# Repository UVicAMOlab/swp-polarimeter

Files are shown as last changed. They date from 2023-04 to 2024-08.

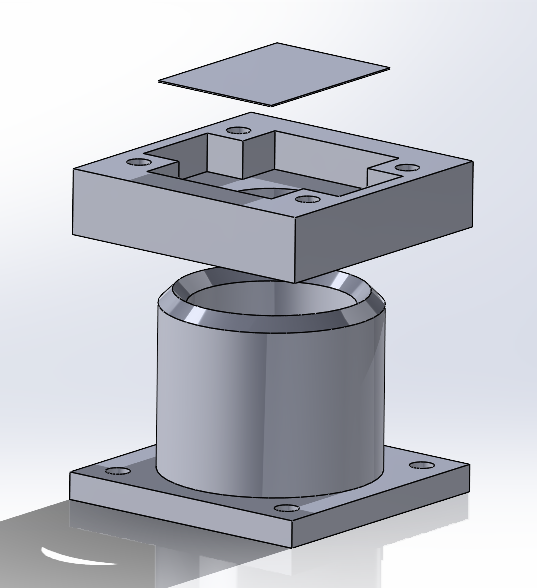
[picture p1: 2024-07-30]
CAD-parts-2024/3D_Printed_Parts/Exploded_View_of_DiodeHousing_with_Polarizer.png

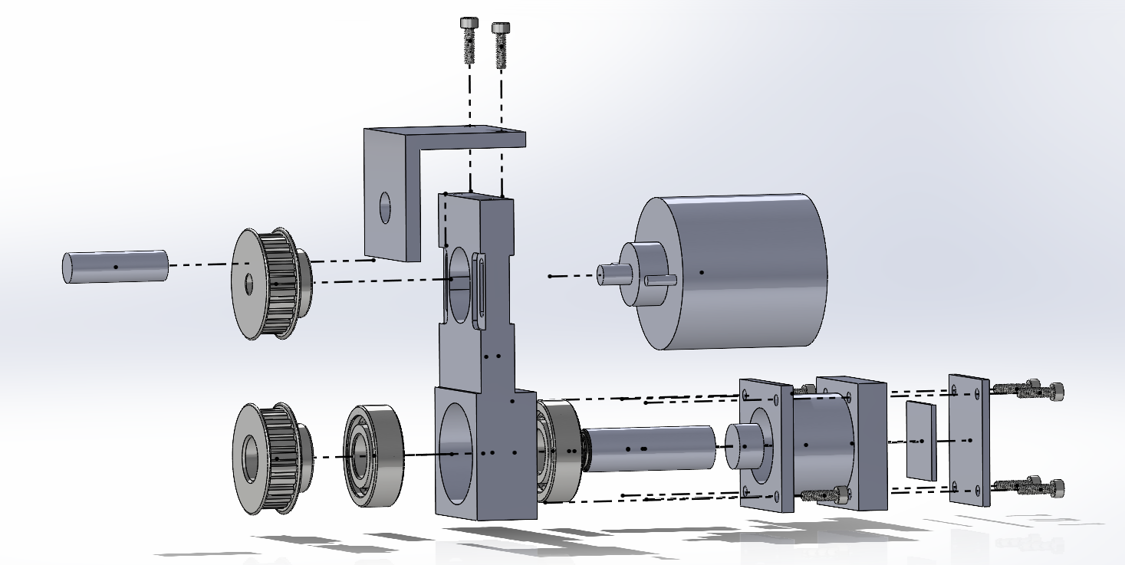
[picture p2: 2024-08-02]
resources-and-documentation/assembly/Mechanical_Assembly_Exploded_View.png

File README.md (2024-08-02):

## Spinning Waveplate Polarimeter

*Using a rotating quarter waveplate, a photodiode, and a few Python scripts, we can produce real-time visualization of the polarization state of incident light. This fully integrated system is easily calibrated and an affordable alternative to other fussy optical technologies making it ideal for research laboratories and educational environments.*

# Real-time Detection of Polarization of Incident Light

Initially, we use the API provided by the DAQ hat to acquire a fixed number of samples for processing; typically, this is 1000 samples at 20 ksps when the waveplate is spinning between 4500 to 5500 RPM. The raw data input is then divided into segments. Each segment is numerically integrated to determine the Fourier coefficients, and furthermore, the Stokes parameters and polarization state. To minimize any statistical errors, the mean result over several segments is considered and the display is refreshed at a rate of 4 Hz.

The reconstruction of the Stokes vector is achieved by calculating the incident intensity upon the rotating waveplate as a function of the rotation angle when aligned horizontally. We assume that the waveplate has some arbitrary retardance instead of considering a precisely calibrated quarter waveplate. Lastly, using the orthogonality of trigonometric functions we can extract the Stokes parameters S<sub>0</sub>, S<sub>1</sub>, S<sub>2</sub> and S<sub>3</sub>. Using the Stokes parameters, the degree of polarization of the incident light is also obtained through a trivial calculation.

Please see our more rigorous [explanation]#(REPLACE WITH PAPER LOCATION) and [analysis](https://github.com/UVicAMOlab/swp-polarimeter/blob/main/resources-and-documentation/analysis/Polarimeter_Analysis.pdf) for more details.

# Information Obtained from Polarimeter

The continuous data input through the Raspberry Pi's MCC DAQ hat along with the included software allows for the real-time determination and visualization of several polarization parameters. These include:

- Polarization ellipse/type of polarization (2D or 3D available)
- Stokes parameters as bar graph
- Poincaré sphere
- Degree of polarization
- Mean input signal over several segments of data
- Waveform incident on photodiode

# Getting Started

**PHYSICAL APPARATUS:**

Our spinning waveplate polarimeter utilizes a high-speed motor connected to an internally threaded rotating lens tube by a timing belt. Low friction ball bearings press-fit into the main base housing the lens tube. A polymer zero-order waveplate is threaded inside the tube. At the top of the timing belt, the upper gear contains a small magnet that is detected by the hall sensor which provides a reference angle and acquisition triggering. We chose a photodiode with an integrated transimpedance of 100 $k\Omega$ followed by a second non-inverting opamp with a variable gain from 1 to 11 via an accessible 10 $k\Omega$ potentiometer. The photodetection circuitry is housed by a 3D printed adapter plate which contains a thick polarizing sheet. The photodiode and hall sensor trigger outputs are sent into the Raspberry Pi computer which is modified with a 12 bit, 100 ksps data acquisition hat (DAQ).

All mechanical designs are open source and can be found in the [CAD-parts-2024 folder](https://github.com/UVicAMOlab/swp-polarimeter/blob/main/CAD-parts-2024).

**PCB:**

All PCB designs are open source. Designs and supplemental documentation can be found in the [circuit-pcb-2024 folder](https://github.com/UVicAMOlab/swp-polarimeter/blob/main/circuit-pcb-2024).

**CODE INSTALLATION:**

For code installation simply download the .zip file or clone the repository. All necessary code is provided in the [code folder](https://github.com/UVicAMOlab/swp-polarimeter/blob/main/code). Before operation, the [daqhats folder](https://github.com/mccdaq/daqhats/tree/master/daqhats) for operating the MCC 118 DAQ HAT must be downloaded and placed in the code folder.

## Operation Instructions

Once the apparatus has been assembled and the code is available through a computer with data acquisition it is time to begin aligning the laser beam onto the photodiode ensuring it is collimated and securely fastened. 

Please see our [calibration guide](https://github.com/UVicAMOlab/swp-polarimeter/tree/main/resources-and-documentation/calibration/SWP_Calibration_Guide.pdf) for detailed instructions on device calibration.

To access the user interface, ensure the laser is on and the polarimeter is running at your desired settings. Run the file "polvis.py" to view the real time visualization of the optical state of the incident light. Warnings printed by "polvis.py" will assist in troubleshooting by diagnosing issues and suggesting remedies.

# Known Limitations

**Non-Ideal Quarter Waveplate:**

Due to the dispersive and birefringent effects of light on the waveplate it is possible that the phase shift between the fast and slow axes may deviate from the quarter waveplate condition of $\delta=\pi/2$. This can lead to an incorrect reconstruction of the polarization state. Although calibration corrects for this wavelength-dependent phase retardance, small variation in the retardance may occur over several days while lasing at a fixed wavelength. Moreover, large variation is seen with changes to the incident wavelength. For this reason, waveplate phase retardance calibration should be performed before each session using the polarimeter.

**DC Offset:**

The issue of DC offset from background lighting and dark current is also present. Although our design does not fully correct for dark current, background light is zeroed allowing a vast reduction in total DC offset. Re-calibration for background lighting is at the discretion of the user once the apparatus is stationary in a lab setting.

**Non-Constant Rotation of Quarter Waveplate:**

In practice, the rotation of the quarter waveplate is non-constant. The polarimeter angle however must be known at all points along the trace so the sine and cosine quadratures can be determined. This is accomplished by inferring the angle through linear interpolation between triggers. Residual error arises when the angular velocity is non-constant making linear interpolation inaccurate. We have found that if the quarter waveplate rotates at a high RPM the system can be assumed intrinsically inertially stable meaning changes to angular speed will be gradual over several periods. For this reason, a powerful motor is a key design component.

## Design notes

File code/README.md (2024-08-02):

** Code Overview **
This folder contains all code used to for calibration, data collection, and analysis with the polarimeter. 

The file "gen_default_json.py" is used to initialize the files for storing settings. The created files "daq_settings.json" and "sim_settings.json" should be manually adjusted to the desired paramters of the device or simulation. In contrast, "swp_settings.json" will be populated mostly by the data collected during calibration. However, for data recording a filename must be manually entered in the log_data_file parameter. The files "calibrate_background.py", "calibrate_trigger_delay.py", and "set_waveplate.py" are used for calibration. For proper calibration procedures refer to "calibration_procedure.pdf" in the documentation folder. The file "estimate_motor_jitter.py" is used to validate the selected motor for use with the device; if the period changes by more than one digitally-discritized unit between consecutive rotations, then jitter should be considered an issue and the motor should be replaced. To run the device, "polvis.py" is used and the desired display, logging, and simulation/real-time options can be specified within the program. The files "swptools.py" and "daqhats_utils.py" contain custom libraries.

Before use, the daqhats library should be downloaded from https://github.com/mccdaq/daqhats and the contained folder daqhats should be moved or copied to this folder ("code"). 

Python 3.12 is required for operation. Required standard libraries are numpy, matplotlib.pyplot, datetime, 

All code is open sourced and can be downloaded or distributed freely.

*Brendan Mackey*

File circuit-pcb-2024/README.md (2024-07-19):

# Spinning Waveplate Polarimeter Photodiode Circuit

This directory contains the KiCad 8.0 files for the SWP's photodiode circuit, as well as the files necessary to order the circuit board from PCBWay and parts from DigiKey. 

There is also a PDF that goes in depth into how the circuit works, how it is laid out, and how to go about modifying it.

### Note: The circuit and all files are open source. You are free to use them as you would like, I only ask you keep them open source.

# Ordering your own

To order your own photodiode circuit, you need accounts on DigiKey as well as PCBWay. Other PCB manufacturers work, but you may need to send them different files. As of July 2024, excluding shipping, the parts cost less than $15, and the boards cost $5.

## DigiKey

SWPBOM.csv is a bill of materials for this circuit. You can drag and drop this file into DigiKey's 'Upload a file' option within the cart. On the columns labeled 'Qty' and 'DigiKey Part Number,' select 'Quantity' and 'DigiKey Part Number' respectively. You may also want to select 'Customer Reference' on the 'Reference' column. This way, the bags will be labeled with part numbers, making soldering easy. Then, all the items for one board will be added to your cart.

Digikey may give you a better value option (10 resistors can cost less than 3), and you can do this. No loss saving money!

## PCBWay

SWPGerbers.zip is a zipped Gerber file generated to PCBWay's standards. You don't need to unzip this, you can simply input it directly into PCBWay. Input 40mm x 50mm for the PCB size, 2-layer and a quantity of 5. Everything else should be default settings. You can choose to use a different solder mask colour to get a different style board!

# More Info

The SWPPhotodiodeGuide.pdf file gives a detailed description of the circuit and how to use it. If you want to edit the KiCad files, it's best to read this beforehand

## Editing

You are free to download the KiCad files and open them in KiCad 8.0 or newer. Suggestions for editing are given in SWPPhotodiodeGuide.pdf.

*Owen Sandner*

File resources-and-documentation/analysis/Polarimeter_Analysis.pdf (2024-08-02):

# Polarimeter Analysis

UVicAMO

## 1 Calibrating and Correcting the Retardance of a Waveplate

### 1.1 Importance of Waveplate Calibration

Our method involves rotating a quarter waveplate in front of a linear polarizer to extract the Stokes vectors of a beam of light. Since we are relatively insensitive to (polarization independant) losses, we can assume an ideal linear polarizer – that is we can assume that the transmission of the orthoganally polarized light is negligably small. However, we are likely not justified in assuming an ideal quarter waveplate. Supposing even that we have narrowband (or even monochromatic) light, a waveplate will typically have a wavelength-dependant phase delay. For a quarter waveplate, the relative delay between its fast and slow axes is δ =
2n+1
2

π, where n is an integer. The wavelength dependence can be minimized for a so-called “zero-order” waveplate¹
, i.e. on for which n = 0, is used. Even for zero-order waveplates however, there is still some wavelength dependence and so we can not assume that we have a real QWP for all angles.
A waveplate with fast axis horizontal will create a relative phase shift δ between the horizontal and vertical polarization components. If we are working with fully polarized states, the Jones formalism may be used and the corresponding Jones matrix is given by²
Eh
Ev
→
1 0
0 e
| iδ Eh
Ev
=
Eh
e

iδEv

(1)

### 1.2 A Method for Measuring δ

A simple method to measure the phase delay δ is to rotate the waveplate in between two polarizers. The polarizers can either be crossed or parallel. Experimentally it may be easier to align cross polarizers since it is easier to measure a minimum than a maximum. Suppose that the first polarizer is aligned horizontally. Regardless of the input light, it will be completely polarized horizontally with some amplitude E0 and intensity I ∝ |E0|

2
. Since it is completely polarized, we may work in the simpler Jones formalism. The output field is then:

E⃗

out = PhWδ,θE⃗
in =
| 1 0

0 0 A B
C D E0
0
= AE⃗
0 | (2)

. . . where Wδ,θ is the matrix corresponding to a waveplate of phase shift δ rotated an angle θ with respect to the horizontal. The output intensity is then

Iδ(θ) = |A|

2
I0 | (3)

With crossed polarizers, the intensity is similarly

Iδ,⊥(θ) = |B|

2
I0 | (4)

1Actually there are two classes of zero-order waveplates, “true” and “effective” zero order. For true zero order, the physical delay between a monochromatic beam two polarizations is λ/4. Since this is very hard to make, typically two orthogonally oriented waveplates with order m and m + 1 are cemented together, advancing the beam by (m + 1) and delaying by m quarter wavelengths, which has the same effect at the precise wavelength.
2There is also a global phase shift applied to both beams e

iϕ which is equivalent to simple propagation over a distance L = 2πϕλ. This is not relevant here. Also note that some author prefer to share the phase equally between the two polarizations so the each component gets a phase factor e±iδ/2

The parameters A and B can be obtained via rotating the waveplate in equation 1:

PhWδ,θ = R(θ)PhWδ,0R(−θ)

=

cos θ − sin θ
sin θ | cos θ
1 | 0
0 e

iδ cos θ sin θ
− sin θ cos θ

=

cos²

θ + sin²
θeiδ cos θ sin θ
1 − e

iδ
cos θ sin θ
1 − e

iδ

sin²
θ + cos²

θeiδ
(5)

Thus the intensity as a function of angle is:

Iδ(θ) =

cos⁴

θ + sin⁴
θ + 2 cos²

θ sin²
θ cos δ
I0 | (6)

Note that if δ =

2n+1
2

π (with integer n), then Iδ(θ) = I0 which is interesting. If δ = nπ then Iδ(θ) =
cos²

θ − sin²
θ

2
= cos² 2θ and we have perfect “visibility”. Note as well that with the crossed polarizer result we have |B|

2 = sin 4θ sin δ
2
To extract the phase δ, we may align the polarizers in our setup and observe the resultant trace. An example of this is shown in figure 1. There will be maxima and minima which can be used to extract the phase: taking the derivative of equation 6 with respect to θ:

d
dθ Iδ(θ) = -2 cos δ sin 2θ cos 2θ − 4 cos θ sin θ

cos²
θ − sin θ

2
I0
= [sin 4θ (cos δ − 1)] I0 | (7)

Setting this to zero we have either that δ = 0 (as a special case - recall δ is fixed) or that θ =

nπ
4

. For
even n, the third term in equation 6 vanishes and either the sine or cosine gives 1 (the other is 0). This is the maximum at I = I0. For odd n the result is a minimum. In this case sin θ = cos θ = 1/

√
2 and we have.

Imin

Imax

≡ η =

1 + cos δ
2

(8)

We can thus find the phase delay of a waveplate as:

δ = arccos (2η − 1) | (9)

Figure 1: Using a red LED to calibrate our QWP. We find that for this wavelength (λ ≈ 630 nm) we have a λ/3.0 plate! An overall phase of 0.69 rad was added to equation 6 to match the trigger origin of the motor.

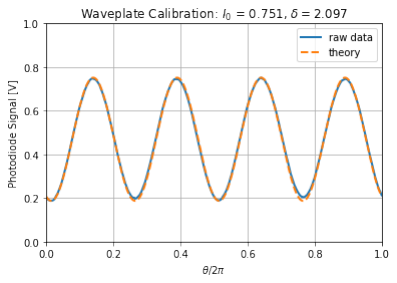
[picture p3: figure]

### 1.3 Correcting for Non-Ideal Waveplates

Given that we know the true phase shift of our waveplate, can we still extract the Stokes parameters as before? It turns out that we can . . .

## 2 Expected Intensity, Given Stokes Vector

### 2.1 Mueller Matrix of our system

Consider a monochromatic field with vacuum wavelength λ. A generic waveplate, with phase retardance δ/2 and fast axis horizontal performs the transformation:

Ex → e

iδ/2Ex | (10a)

Ey → e

−iδ/2Ey | (10b)

Since S0 = |Ex|

2 + |Ey|

2 and S1 = |Ex|

2 − |Ey|

2
, neither are affected by the waveplate as expected intuitively for a horizontal/vertical fast/slow axis. However, both S2 and S3 are affected. To see this, we can use Euler’s identity:

S2 = ExE

∗
y + E

∗
xEy
→ e

iδExE

∗
y + e

−iδE

∗
xEy

= cos δ

ExE

∗
y + E

∗
xEy
+ isin δ
ExE

∗
y − E

∗
xEy

S2 → cos δS2 + sin δS3

Similarly, S3 → cos δS3 − sin δS2. Writing this as a matrix equation yeilds the Mueller matrix for a arbitrary waveplate:

Wδ,0

- =

1 0 | 0 | 0
0 1 | 0 | 0
0 0 | cos δ | sin δ
0 0 − sin δ cos δ

(11)

To find the matrix corresponding to a waveplate rotated an angle θ to the horizontal we apply the rotation matrix³
:

R(θ) =

1 | 0 | 0 | 0
0 cos 2θ − sin 2θ 0
0 sin 2θ | cos 2θ | 0
0 | 0 | 0 | 1

(12)

. . . so that
Wδ,θ = R(θ)Wδ,0
◦R(−θ) | (13)

The end result of this is then sent through a linear polarizer aligned horizontally, having matrix

P0 =

1
2

1 1 0 0
1 1 0 0
0 0 0 0
0 0 0 0

(14)

We can just blast away at the whole expression now but many of the terms will be redundant for our purposes. Recall that all that we measure is the intesity, givent by S0. Note that, writing the rotated waveplate as some abstract matrix, we have that the stokes vector after passage through the system is

3Note that the 2θ comes about in taking the square to find the intensity.

S⃗′ =

I(θ)
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
1 1 0 0
1 1 0 0
0 0 0 0
0 0 0 0

W11 | W12 | W13 | W14
W21 | W22 | W23 | W24
W31 | W32 | W33 | W34
W41 | W42 | W43 | W44

S0
S1
S2
S3

(15)

From this, we can just take the first component of the output Stokes vector to find:

I(θ) = W11 + W21
2

S0 +

W12 + W22
2

S1 +

W13 + W23
2

S2 +

W41 + W24
2
S3 | (16)

so we just need to find the first two rows of the rotated waveplate. Actually it isn’t too much more work doing the whole calculation but this gives the answer in terms of what we calculate. Grinding out equation 13, we get:

R(θ) =

1 | 0 | 0 | 0
0 | cos² 2θ + cos δ sin²
2θ | sin 2θ cos 2θ(1 − cos δ) − sin 2θ sin δ
0 sin 2θ cos 2θ(1 − cos δ) sin²
| | 2θ + cos δ cos² 2θ | cos 2θ sin δ
0 | sin δ sin 2θ | − sin δ cos 2θ | cos δ

(17)

Finally, plugging this back into equation 16, we have the desired result of the intensity as a function of Stokes parameters:

I(θ) = 1
2

S0 +

cos² 2θ + cos δ sin²
2θ
2

S1 +

sin 2θ cos 2θ(1 − cos δ)
2

S2 −

sin 2θ sin δ
2
S3 | (18)

Finally, by employing trigonometric half angle formulae (sin 2x = 2 sin x cos x, 2 sin² x = 1 − cos 2x, and 2 cos² x = 1 + cos 2x) we arrive at:

I(θ) = 1
2
S0 +
1 + cos δ
2
S1
−
sin δ
2

S3

sin 2θ +
1 − cos δ
4

S1

cos 4θ +
1 − cos δ
4

S2

sin 4θ (19)

Note that in the limit of an ideal quarter waveplate (δ = π/2) this becomes

I(θ) = 2S0 + S1
4

−

S3
2

sin 2θ +

S1
4

cos 4θ +

S2
4
S2 sin 4θ | (20)

as is found in the literature.

## 3 Extracting the Stokes Vectors

The intensity through a rotating waveplate of retardance δ followed by a polarizer aligned horizontally is given by:

I(θ) = 1
2
S0 +

1 + cos δ
2

S1

−
sin δ
2

S3

sin 2θ +
1 − cos δ
4

S1

cos 4θ +
1 − cos δ
4

S2

sin 4θ
≡ A + B sin 2θ + C cos 4θ + D sin 4θ | (21)

Using the orthogonality of trigonometric functions, we can write:

S1 =

4
π(1 − cos δ)

Z 2π

0

I(θ) cos 4θdθ | (22a)

S2 =

4
π(1 − cos δ)

Z 2π

0

I(θ) sin 4θdθ | (22b)

S3 = −

2
π sin δ

Z 2π

0

I(θ) sin 2θdθ | (22c)

S0 =

1
π

Z 2π

0

I(θ)dθ −

1 + cos δ
2
S1 | (22d)

## 4 A Few Results from Fourier Theory

### 4.1 Orthogonality of Sinusoidal Functions

Let T be some interval and define ω0 ≡ 2π/T. Consider sines and cosines with frequency equal to some integer multiple of ω0:
fω0 ∈ {sin (nω0t), cos (mω0t)} . . . n, m ∈ Z | (23)

These functions are orthogonal when integrated over a period T, specifically:
Z T

0

sin (nω0t) sin (mω0t) dt =

π
ω0
δmn | (24a)
Z T

0

cos (nω0t) cos (mω0t) dt =

π
ω0
δmn | (24b)
Z T

0

sin (nω0t) cos (mω0t) dt = 0 | (24c)

To see this, it is helpful to use the identities:

sin (nω0t) sin (mω0t) = 1
2
[cos((n − m) ω0t) − cos((n + m) ω0t)] | (25a)

cos (nω0t) cos (mω0t) = 1
2
[cos((n − m) ω0t) + cos((n + m) ω0t)] | (25b)

sin (nω0t) cos (mω0t) = 1
2
[sin((n + m) ω0t) − sin((n − m) ω0t)] | (25c)

If n = m, the identities give (1−cos 2nω0t)/2 = sin² nω0t, (1+cos 2nω0t)/2 = cos² nω0t, and (sin 2nω0t)/2 respectively. Regardless of whether or not n = m, the frequency arguments to the sine and cosine terms are still just integer multiples of ω0, since 2n, n − m, and n + m are just some other integer. Thus every term in 25 can be written as sin(Nω0t) or cos(Nω0t). This means that the integral of these terms over a period vanishes:

Z T =2π/ω0

0

sin(Nω0t)dt = −

1
Nω0

[cos (2Nπ) − cos 0] = 1 − 1 Nω0

= 0

Z T =2π/ω0

0

cos(Nω0t)dt =

1
Nω0

[sin (2Nπ) − sin 0] = 0 − 0 Nω0

= 0

The only possible non-zero term is thus the constant term, occurring when n = m, for which:
Z T

0

1
2

dt =

T
2

=

π
ω0

(26)

Thus, almost all terms in equation 24a, written using eq. 25 are identically zero. The only exception is when n = m in 24aa and 24ab, for which equation 26 holds. Written in terms of the dirac delta function then, this completes the proof.

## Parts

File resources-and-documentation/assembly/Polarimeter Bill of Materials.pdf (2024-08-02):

Bill of Materials | August 2024
Part Name | Vendor | Part Number | Price ($USD)

Optics
Mounted Zero-Order QWP | Thorlabs | WPQ05ME-780 | 291.16
2”x 2” Diffuse Polarizer Sheet | Thorlabs | LPNIRE2X2 | 102.48
| | Optics Total | 393.64
Mechanics and Opto-Mechanics
24V DC Motor | Amazon | XD3420 | 29.53
Hall Switch | YOYCart | CHE12-10NB-H710 NJK-5002D | 4.66
2” Lens Tube | Thorlabs | SM05L20 | 21.07
2x ½’’ Optical Post | Thorlabs | TR20/M | 10.76
2x ½’’ Post Holder and Base | Thorlabs | PH2, BA1S | 29.16
2x Timing Pulley, 8mm Shaft† | McMaster | 1277N721 | 35.04
Drive/Timing Belt† | McMaster | 6484K2 | 6.18
2x Ball Bearing† | McMaster | 5972K104 | 12.16
6x M4 Hex Screws | McMaster | 91290A164 | 0.96
2x M4 Phillips Screws | McMaster | 92467A219 | 0.38
4x M4 Nuts | McMaster | 90591A255 | 0.06
| | Opto-Mechanics Total | 149.96
Custom Parts | | Extra Information
PLA Photodiode Mount (Raw Material) | Custom | $0.02/g, 34.3g | 0.69
Aluminum Body (Raw Material) | Custom | Machine Shop Quote | 18.09
Machining Time* | N/A | $25.32/hr, 7hr | 177.24
| | Custom Parts Total | 196.02
Raspberry Pi
Raspberry Pi 3 B | DigiKey | 2648-SC0022-ND | 35.00
MCC118 DAQ HAT | DigiKey | 1286-6069-410-000-ND | 99.00
| Raspberry Pi Total | | 134.00
Photodiode Electronics
Printed Circuit Board | PCBWay | Custom Order, 2-Layer | 5.00
OPT101 Photodiode-TI Amp | DigiKey | 296-23090-5-ND | 8.57
RM107 Rotary Switch | DigiKey | CKN10705-ND | 3.38
Header Connectors x2 | DigiKey | 900-0022232021-ND | 0.42

Part Name | Vendor | Part Number | Price ($USD)
SMD Resistors** | DigiKey | Mixed Value** | 1.10
SMD Capacitors** | DigiKey | Mixed Value** | 1.99
| | Electronics Total | 20.46
| Total ($USD) | | 894.08

†Exact McMaster parts may no longer be in production. As long as parts have the same properties (Same pitch, OD, shaft diameter; correct belt length), any combination will work.

*Note that machining costs include modification of one timing pulley and lens tube.

**See github: circuit-pcb-2024>to-order>SWPBOM.csv for detailed part breakdown.

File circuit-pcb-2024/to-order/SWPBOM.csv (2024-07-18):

Reference | Value | Datasheet | Footprint | Qty | DNP | DigiKey Part Number
C7 | 0pF | ~ | Capacitor_SMD:C_0603_1608Metric_Pad1.08x0.95mm_HandSolder | 1
C6 | 2.5pF | ~ | Capacitor_SMD:C_0603_1608Metric_Pad1.08x0.95mm_HandSolder | 1 |  | 13-CC0603BRNPO9BN2R5CT-ND
R6 | 20M | ~ | Resistor_SMD:R_0603_1608Metric_Pad0.98x0.95mm_HandSolder | 1 |  | 13-RC0603JR-0720MLCT-ND
PD1 | ~ |  | Package_DIP:DIP-8_W7.62mm_LongPads | 1 |  | 296-23090-5-ND
R8 | 1k | ~ | Resistor_SMD:R_0603_1608Metric_Pad0.98x0.95mm_HandSolder | 1 |  | 311-1.00KHRCT-ND
R1 | 3.3k | ~ | Resistor_SMD:R_0603_1608Metric_Pad0.98x0.95mm_HandSolder | 1 |  | 311-3.30KHRCT-ND
R2 | 22k | ~ | Resistor_SMD:R_0603_1608Metric_Pad0.98x0.95mm_HandSolder | 1 |  | 311-22KGRCT-ND
R3 | 43k | ~ | Resistor_SMD:R_0603_1608Metric_Pad0.98x0.95mm_HandSolder | 1 |  | 311-43.0KHRCT-ND
R9 | 53k | ~ | Resistor_SMD:R_0603_1608Metric_Pad0.98x0.95mm_HandSolder | 1 |  | 311-53.6KHRCT-ND
R4 | 220k | ~ | Resistor_SMD:R_0603_1608Metric_Pad0.98x0.95mm_HandSolder | 1 |  | 311-220KGRCT-ND
R5 | 1M | ~ | Resistor_SMD:R_0603_1608Metric_Pad0.98x0.95mm_HandSolder | 1 |  | 311-1.00MHRCT-ND
C8,C9 | 100pF | ~ | Capacitor_SMD:C_0603_1608Metric_Pad1.08x0.95mm_HandSolder | 2 |  | 311-1069-1-ND
C11 | 100nF | ~ | Capacitor_SMD:C_0805_2012Metric_Pad1.18x1.45mm_HandSolder | 1 |  | 311-1140-1-ND
C10 | 1uF | ~ | Capacitor_SMD:C_2225_5664Metric_Pad1.80x6.60mm_HandSolder | 1 |  | 445-2304-1-ND
C5 | 51pF | ~ | Capacitor_SMD:C_0603_1608Metric_Pad1.08x0.95mm_HandSolder | 1 |  | 478-10326-1-ND
C4 | 39pF | ~ | Capacitor_SMD:C_0603_1608Metric_Pad1.08x0.95mm_HandSolder | 1 |  | 478-KGM15ACG1H390JTCT-ND
C2,C3 | 56pF | ~ | Capacitor_SMD:C_0603_1608Metric_Pad1.08x0.95mm_HandSolder | 2 |  | 478-KGM15ACG1H560JTCT-ND
C1 | 82pF | ~ | Capacitor_SMD:C_0603_1608Metric_Pad1.08x0.95mm_HandSolder | 1 |  | 478-KGM15ACG1H820JTCT-ND
C12 | 10nF | ~ | Capacitor_SMD:C_0603_1608Metric_Pad1.08x0.95mm_HandSolder | 1 |  | 490-4781-1-ND
R7 | 50M | ~ | Resistor_SMD:R_0603_1608Metric_Pad0.98x0.95mm_HandSolder | 1 |  | 541-47MAHCT-ND
J1,J2 | Conn_01x02_Pin | ~ | Connector_Molex:Molex_KK-254_AE-6410-02A_1x02_P2.54mm_Vertical | 2 |  | 900-0022232021-ND
SW1 | SW_Rotary_1x7_MP | ~ | UVAMOFootprints:RM107-RotarySwitch | 1 |  | CKN10705-ND

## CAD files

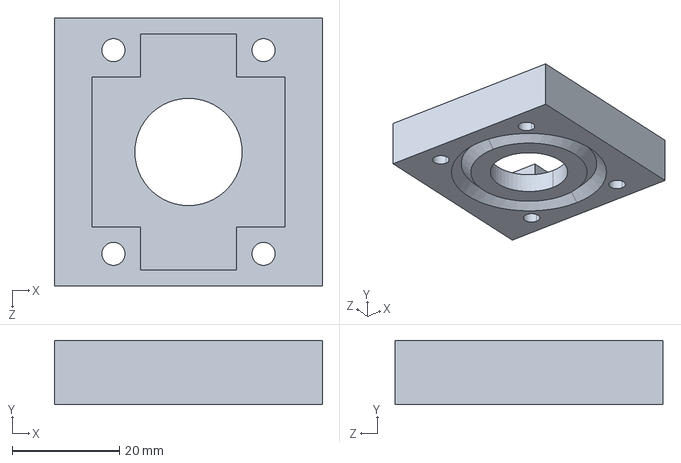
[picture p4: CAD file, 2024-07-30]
CAD-parts-2024/3D_Printed_Parts/Polarimeter_DiodeHolder_Top.STEP
50.0 x 12.0 x 50.0 mm

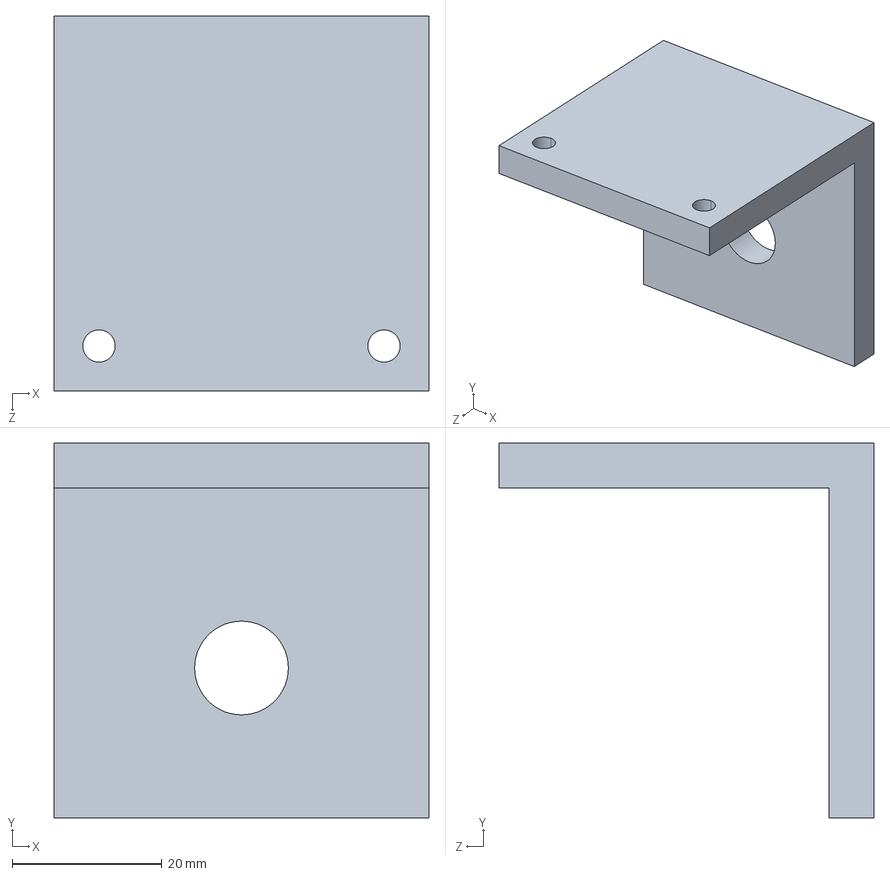
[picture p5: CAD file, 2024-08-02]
CAD-parts-2024/Machined_Parts_CAD_and_Drawings/Hall_Sensor_Bracket.STEP
50.0 x 50.0 x 50.0 mm

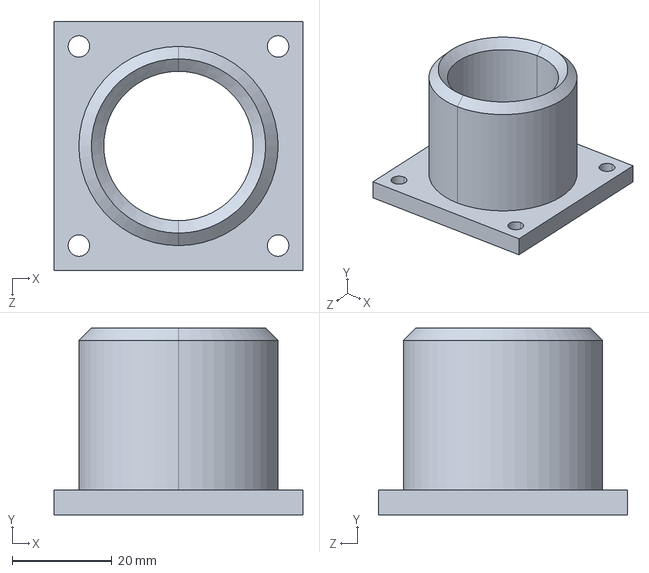
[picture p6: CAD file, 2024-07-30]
CAD-parts-2024/3D_Printed_Parts/Polarimeter_DiodeHolder_Base.STEP
50.0 x 37.5 x 50.0 mm

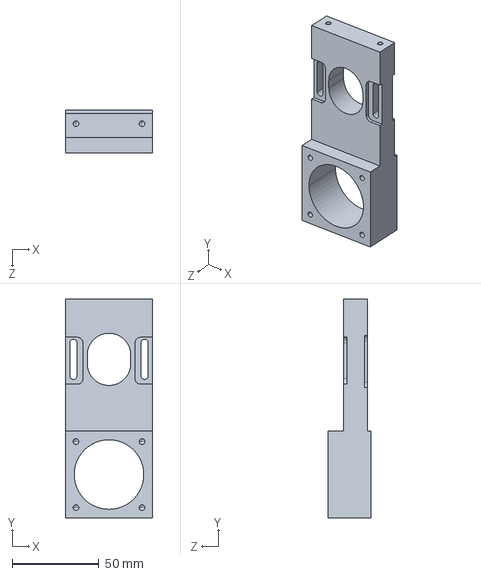
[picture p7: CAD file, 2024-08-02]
CAD-parts-2024/Machined_Parts_CAD_and_Drawings/Polarimeter_Body.STEP
50.0 x 126.0 x 25.0 mm

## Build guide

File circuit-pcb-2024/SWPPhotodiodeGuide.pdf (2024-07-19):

Owen Sandner | SWP Photodiode Circuit | July 19, 2024

This note is for construction of the UVAMO Spinning Waveplate Polarimeter’s (SWP) pho-

todiode amplifier, as well as a guide to build one yourself. This is followed by a modification

guide, including design considerations for those wanting to build their own photodiode.

We will start with an introduction to photodetection using a photodiode, then we will

discuss the circuit used in the UVAMO SWP.

## 1 Photodetection

The goal of photodetection is to measure the intensity of light. This is simple using a silicon

PIN junction photodiode and a transimpedance amplifier.

### 1.1 Reverse Biased Photodiodes

Generally, diodes allow current to pass through them in only one direction with a constant

voltage drop. This is usually accomplished by connecting a positively doped semiconductor

with a negatively doped one. This allows current to flow one way while blocking it from

flowing the other way, up to a breakdown voltage.

Certain specialized diodes, known as photodiodes, function in reverse bias as shown below.

When a photon of sufficient energy¹
- and hence a sufficient frequency - strikes the surface

of the diode, an electron is released through the photoelectric effect. The hole it leaves

is quickly filled by another electron being pushed by the bias voltage. As such, when a

sufficiently intense beam is incident on the photodiode, a current known as a photocurrent

is generated in the direction of the reverse bias. This is the photodiode’s working principle.

Reverse Biased Photodiode

1This energy is defined by the PIN junction

1 | UVAMO 2024

We use a 780nm laser, so let’s try to find the output current if we strike the photodiode

with 10mW. Assuming every photon of energy Ep =

hc
λ = 1.59eV is converted to an electron,

we would get a current of

10mW ·

eV
1.602 × 10⁻¹⁹J

·

e

−
1.59eV

·

1.602 × 10¹⁹C
e

−

= 6.3mA.

This current is then measured using a transimpedance amplifier.

### 1.2 Transimpedance Amplifier

Unfortunately, it is difficult to measure current directly; instead, we measure the voltage

on either side of a shunt resistor ² and determine the current using Ohm’s Law. The main

issue with this method is the introduction of a new resistor in the circuit. It will affect

the total circuit resistance and hence the current flow, and so it will not give an accurate

measurement.

Using an operational amplifier with a single shunt resistor Rf , we can measure a Vout =

−Rf · iin without introducing any meaningful resistance to the rest of the circuit. This

design, shown in figure ??, is known as a transimpedance amplifier, and is used to accurately

measure current flow.

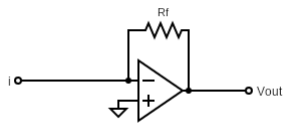
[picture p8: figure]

Transimpedance Amplifier

2This is simply the name given to a known resistor measuring current

## 2 SWP Photodiode Circuit

The circuit used in the UVAMO SWP contains an OPT101, a combined photodiode-transimpedance

integrated circuit. It is attached to a 3d printed case with lips to avoid light entering through

the cracks. It has seven gain stages determined by the input optical power. We chose to

have stages for 500nW, 1µW, 10µW, 100µW, 500µW, 1mW and 5mW.

The OPT101 has an internal 1MΩ feedback resistor, with pins for adding series impedance

to the internal resistor or disabling it and using external impedances. Three gain stages use

the series option, while the other 4 use the disabling option. This is due to the feedback

resistance being lower than 1MΩ. The gain stages are chosen with a 7 position rotary switch

allowing for different feedback resistance values.

The PCB’s power input, as well as the signal output, are in the form of 2-pin Molex

header connectors. These pins allow for any desired connector to be easily soldered and used

with the board. In our case, we have a made-in-house DIN-6 power box, while we connect

the output signal to a BNC for measurement.

The circuit is made in KiCad 8.0.3, and is shown below.

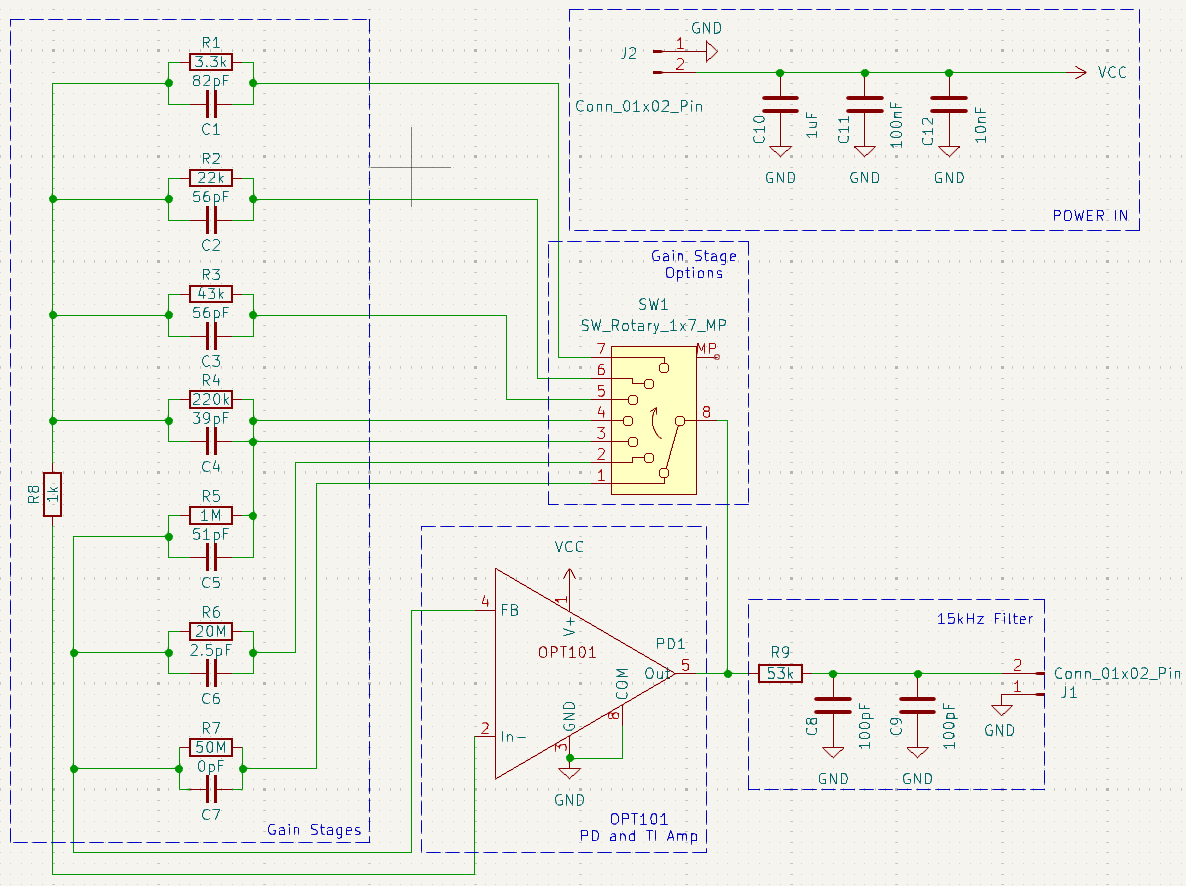
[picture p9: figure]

Photodiode Circuitry

The PCB uses standard resistor/capacitor pairs mounted on opposite sides of the board

to pick gain stages. The rotary switch sends the feedback through different paths, giving

different feedback values at each, hence switching the gain.

KiCad project files can be found on GitHub, along with a bill of materials for the DigiKey

parts. These parts can be ordered by inputting the CSV file into DigiKey’s ‘upload a file’

function. There is also a zipped file containing Gerber and Drill files which can be sent

directly to PCBWay (still zipped) for production. A basic 2-Layer PCB will get 5 boards

made for $5.00 excluding shipping. Note that the board is 40mm x 50mm.

## 3 Making Changes

This section will talk about the possible changes one can make to the circuit to better fit

their needs. An important resource that you should have ready is the OPT101 datasheet,

found on https://www.ti.com/product/OPT101, or on the SWP GitHub with all other

datasheets.

### 3.1 Exchanging Parts

The simplest change one can make is to replace resistors and capacitors on the gain stages.

This allows for different input intensities that are not immediately available on the base

circuit.

To determine the needed feedback resistance, one needs to calculate the gain needed for

the input power to give 12V at maximum. This is 80% of the max 15V supply. There

is no one way to go about this, but it’s a good exercise in unit conversion. Refer to the

OPT101 datasheet for a photosensivity vs. wavelength graph, as this will determine the

needed resistance.

We then need a feedback capacitor to stabilize the feedback loop, whose value is de-

termined by the value of the feedback resistor. Refer again to the OPT101 datasheet for

recommendations for capacitance values. The capacitor corresponding to each resistor is

placed in the resistor’s location on the reverse.

There are two ways to hook up feedback resistors and capacitors. Either they can be

placed in series with the OPT101’s internal 1MΩ feedback resistance by connecting pins 4

and 5 or the internal resistor can be bypassed by connecting pins 2 and 5. On the printed

circuit board, R1-R4 are bypassing, meaning those resistances are the exact gain values,

while R5-R7 are wired in series, meaning the actual gain value has 1MΩ added.

The first major customization is to solder different feedback resistors and capacitors to your gain needs. Use 0603 (1608 metric) chip resistors and capacitors for this, as this is the

pad size on the board. Soldering with a microscope using a temperature around 650 ◦F will

make this trivial.

You may also want to filter the output differently. Simply use different values to achieve

a different RC time constant. To calculate your cutoff frequency, recall that

f−3dB =

1
2πRC .

### 3.2 Editing the Circuit

Using KiCad 8.0.3 or later, you can open the project file. I would ask that you don’t

remove the open source logo, as this project and its derivatives are meant to be

open source.

### 3.2.1 Footprints

You may change footprints for individual parts in the schematic editor. Selecting a part

and pressing ‘E’, you can edit the footprint field. Using the library button (books icon in

footprint field), you can select different parts, or use your own. Remember to use the PCB

editor to reroute tracks and ensure connections.

### 3.2.2 Photodiode

Using a different photodiode will require a lot more work. Recall that the OPT101 is a

monolithic photodiode-transimpedance amplifier IC. You will have to provide smooth reverse

bias and a separate transimpedance stage.

A good option for this purpose is the Thorlabs FDS100 photodiode. Any opamp will work

for transimpedance amplification, but using one labeled for transimpedance amplification

will ensure no issues. A good but relatively pricey option is the OPA847. Its 3.9GHz Gain-

Bandwidth product will ensure that it won’t limit most photodiodes’ bandwidth.

### 3.2.3 Make it your own

If you want something else from the photodetector, you can change the entire circuit, or even

make a new printed circuit board. Keep in mind that changes may affect the performance

of the SWP, and this needs to be taken into account before large changes are made.

For example, you could use the circuit as a blueprint for homemade photodetectors.

When using a good photodiode-transimpedance stage, these can perform on or above the

level of off-the-shelf photodetectors at a much cheaper price. Using parts specifically for your

wavelengths can make them even better at the cost of robustness.

At this point, you are ready to take the photodetector and use it however you’d like!

## 4 Design Considerations

This section will explain the basic design principles followed when making this circuit, as

well as to follow when making edits. There are a few specific goals we want to achieve with

this photodetector:

1. Switchable Gain

We want to be able to set different gain values to avoid railing our opamp. This is

done, as explained above, using a rotary switch in the feedback path. By hooking the

output of the opamp to the common pin of the switch, we can alternate between series

and bypass feedback from the OPT101.

2. Easy Construction

The hardest parts to solder on this board are the resistors and capacitors. 0603 sized

chips were used as they are relatively easy to hand-solder while not taking up too

much space. 0805 may also work, but will take up more space, and may require a

larger board.

3. Low Noise

We don’t have to worry about RF circuit design, as we want to measure sine waves of

frequencies up to 400 Hz. We also want to measure numerous points along this wave,

and so we chose to filter the output to 15 kHz to avoid too much phase shift while still

rejecting pointless signals. Higher frequency signals won’t have even come from our

photodiode as its response time is too slow. This means it is simply electronic noise,

so we get rid of it.

As well, we deal with electronic noise with smart design choices. Using thicker traces

kept as short as possible diminishes possible parasitic effects. We also use a 2-sided

ground plane regularly connected with vias to avoid inductance in ground traces. Power

is filtered to 15Hz in a second order low pass filter. We need not worry about loading

nor phase shift as it’s meant to be a DC signal that is immediately put into an opamp.

4. Compatibility with Polarimeter

This is almost entirely done in conjunction with the case. We need a board that will

(a) Attach to the case,
(b) Have the photodiode’s active area lined up with the input beam,
(c) Block outside light.

These are all done by setting up screws and positions based on the case. For example,

the photodiode is centered in the board, and the case is made with grooves to let the

board sit flush, blocking as much incoming light as possible.

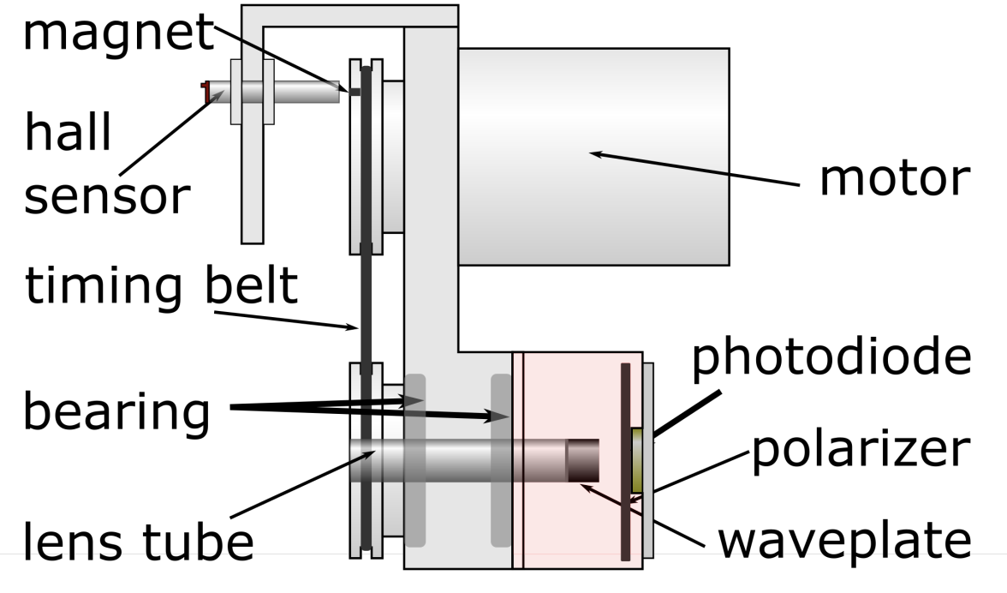
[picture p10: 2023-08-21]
resources-and-documentation/assembly/Diagram_of_Mechanical_Assembly.png

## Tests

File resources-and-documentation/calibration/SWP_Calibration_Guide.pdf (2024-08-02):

Lauren Hall | SWP Calibration | August 2, 2024

This guide serves as a reference to calibrate the UVAMO Spinning Waveplate Polarimeter.

Each constructed polarimeter must be calibrated with multiple parameters, which is done

by running a series of Python scripts. The construction of our Polarimeter has a Raspberry

Pi 3 with an MCC118 DAQ HAT, and the optimal settings from our setup will be outlined

below. All scripts are found within the UVAMO GitHub. It is recommended to perform the

calibration in the same room or area as the experiment. As with any lab procedure, it is

advisable to read the entire document before beginning.

## Initial setup after installation

Depending on the model of DAQ HAT and Raspberry Pi, your setup may have a different

capacity for data acquisition, and initial sampling settings must be set per version. To access

this sampling file, go to settings > daqsettings.json, and change samples_per_channel

and scan_rate as follows. Set samples_per_channel to an integer between 1000 and 10000.

This will designate the volume of samples per channel; at higher volumes, the averaging im-

proves, and at lower volumes, the more accurate the real-time representation. The MCC118

code and DAQ HAT model determine the maximum scan_rate. This code will give an error

for values above 100000. The scan_rate value must accommodate for all the channels. In

our case, we chose 25000, which gives a sampling rate of 50000 across two channels. This

provides the resolution for the sampling. The list of channels and the timeout value can also

be changed within this file, but this is not critical.

## Calibration

Requirements for calibration

Calibration can only be accomplished with a coherent light source of a known monochromatic

wavelength. The laser light must be directed at normal incidence to the photodiode. Other

1 | UVAMO 2024

optical apparatus includes a half-waveplate to obtain horizontally polarized light. Turn on

the motor, and proceed with the following procedures.

Calibrating the trigger delay

The Hall sensor and spinning waveplate are not simultaneous in rotation, therefore the orien-

tation and triggers must be precisely calibrated for the reconstruction of polarization states.

The calibrating light source must be used to complete this step, and one must ensure that

the light is highly circularly polarized. Go to calibrate_trigger_delay.py and run the

script. The script automatically gauges the pulse of the Hall sensor and determines the

delay (∆θ) such that any component the component of the signal that can be represented

as a cos 2(ωt + ∆θ) term is minimized (leaving only the sin 2(ωt + ∆θ) component at fre-

quency 2ω) allowing a zero point to be set. The script then writes the trigger delay to the

swpsettings.json file so that it may be accessed by the main function. It is recommended

to run twice or more to verify the value of the trigger delay. It is also advised to run the script

again every time the polarimeter is partially or fully disassembled, regardless of whether the

polarizing film or hall sensor are removed/replaced.

Adjusting for background light sources

The photodiode utilized in the polarimeter is sensitive to background light which must be

subtracted from the input signal. This step is critical and should be repeated whenever the

environment changes. Go to calibrate_background.py and run the script. Block your

input beam at the source to ensure the background value remains consistent. The script

will verify with the user if the coherent light source is fully blocked before running, and

then automatically save the parameters of the background light. You can now unblock your

beam.

Adjusting the spinning waveplate retardance

The use of a polarizing filter is required for this portion of the calibration, as the sensing

script will now require pure, ”horizontally” polarized light. The previous scripts,

calibrate_background.py and calibrate_trigger_delay.py, must be completed before

this step. Ensure that your input light is linearly polarized along the transmission axis of

the polarizer (referred to a horizontally polarized as convention with this device). This can

be achieved by rotating a polarizer in front of the polarimeter as it is scanning, observing

the raw voltage race output from the device, and finding the polarization direction for which

the upper peaks (Vmax) of the signal are at a maximum. Then, go to set_waveplate.py

and run the script. This script will adjust the spinning waveplate trace retardance for the

selected wavelength. It is advised to run the any time there is a change in wavelength used

or significant change to input angle for the polarimeter. This step concludes the calibration

of the polarimeter.

Verification of drive motor setup

There has been a supplementary script added to help assess the efficacy of the chosen drive

motor, and whether or not the motor has any rotational inconsistency. Go to

estimate_motor_jitter.py and run the script. This function measures what the mean

period of rotation is, as well as the maximum, minimum, and relative error of the mean. It

would be meaningful to run this script more than once per setup, or whenever the motor

speed has changed. For our polarimeter, we noted that these values did not change more

than one discretized value per cycle. If a change of more than one discritized period is

observed consistently, then an alternative motor should be used.

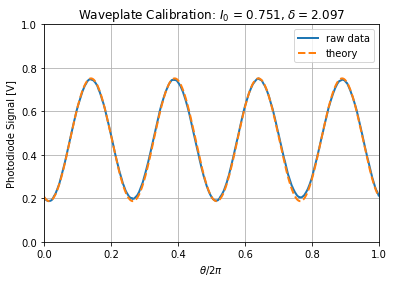
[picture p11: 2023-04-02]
resources-and-documentation/calibration/wave_plate_cal.png

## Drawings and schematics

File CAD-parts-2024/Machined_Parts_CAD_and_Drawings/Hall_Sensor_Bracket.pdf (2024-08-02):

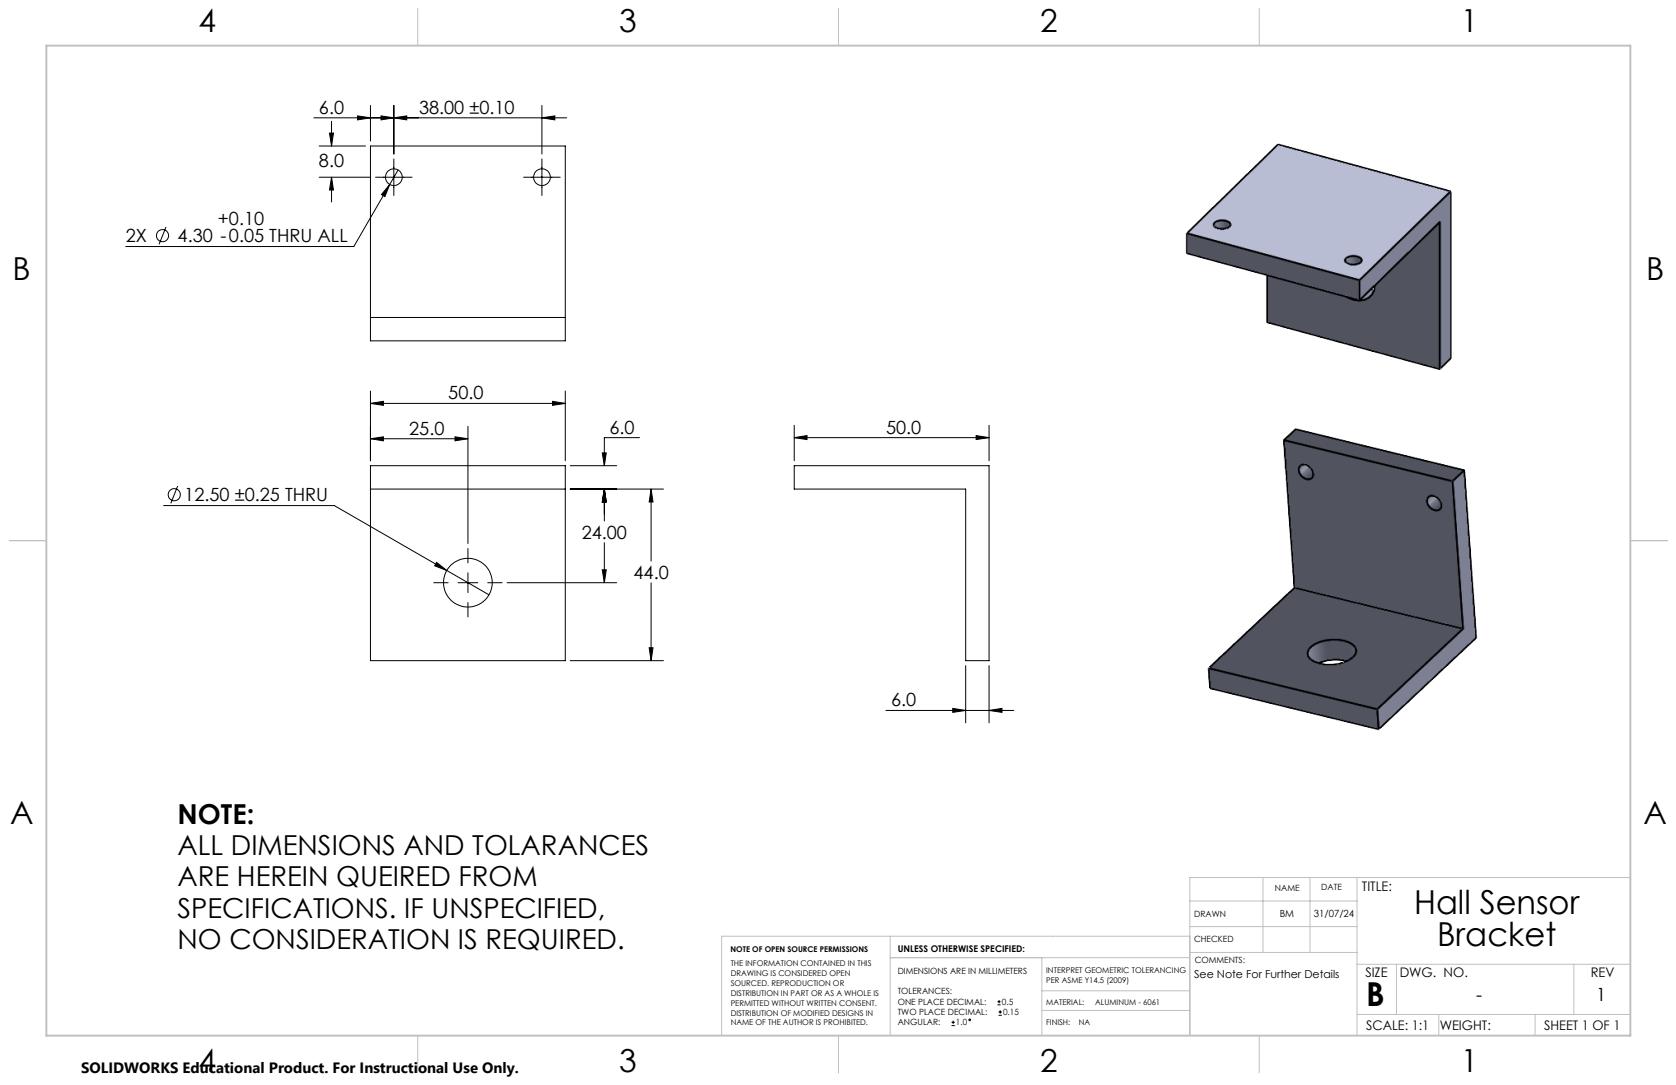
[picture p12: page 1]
12.50 ±0.25 THRU; 0.05 THRU ALL; FINISH: NA; MATERIAL: ALUMINUM - 6061

NOTE:
ALL DIMENSIONS AND TOLARANCES
ARE HEREIN QUEIRED FROM
SPECIFICATIONS. IF UNSPECIFIED,
NO CONSIDERATION IS REQUIRED.

NAME | DATE | TITLE: Hall Sensor Bracket

DRAWN | BM | 31/07/24

CHECKED

NOTE OF OPEN SOURCE PERMISSIONS THE INFORMATION CONTAINED IN THIS DRAWING IS CONSIDERED OPEN SOURCED. REPRODUCTION OR DISTRIBUTION IN PART OR AS A WHOLE IS PERMITTED WITHOUT WRITTEN CONSENT. DISTRIBUTION OF MODIFIED DESIGNS IN NAME OF THE AUTHOR IS PROHIBITED. | UNLESS OTHERWISE SPECIFIED:

COMMENTS:
See Note For Further Details

DIMENSIONS ARE IN MILLIMETERS TOLERANCES: ONE PLACE DECIMAL: 0.5 TWO PLACE DECIMAL: 0.15 ANGULAR: 1.0 | INTERPRET GEOMETRIC TOLERANCING PER ASME Y14.5 (2009)

SIZE B | DWG. NO. - 1 | REV

SCALE: 1:1 | WEIGHT: | SHEET 1 OF 1

SOLIDWORKS Educational Product. For Instructional Use Only.

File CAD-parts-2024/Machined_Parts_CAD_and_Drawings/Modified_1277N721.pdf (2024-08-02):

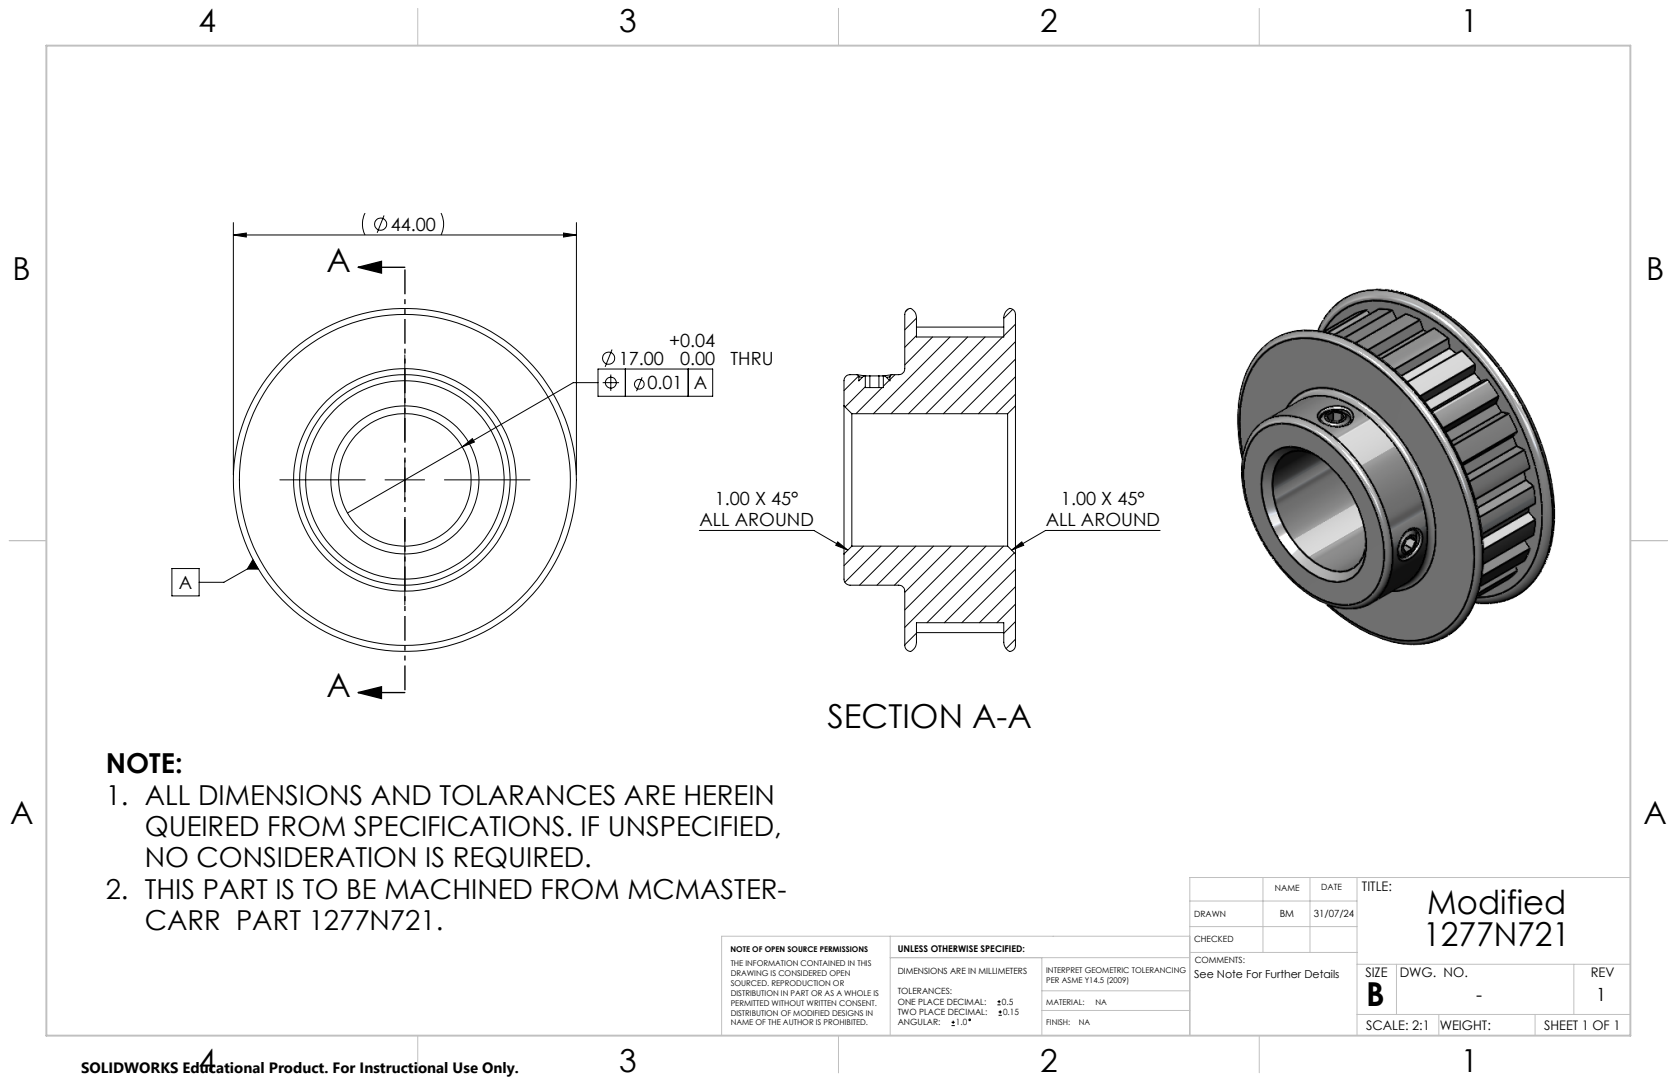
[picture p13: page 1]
0.00 THRU 0.01 A; 1.00 X 45° ALL AROUND; SECTION A-A; CARR PART 1277N721.; Modified; FINISH: NA; MATERIAL: NA

NOTE:
1. ALL DIMENSIONS AND TOLARANCES ARE HEREIN

QUEIRED FROM SPECIFICATIONS. IF UNSPECIFIED,
NO CONSIDERATION IS REQUIRED.
2. THIS PART IS TO BE MACHINED FROM MCMASTER-

NAME | DATE | TITLE: 1277N721

DRAWN | BM | 31/07/24

CHECKED

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

COMMENTS:
See Note For Further Details

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

SIZE B | DWG. NO. - 1 | REV

SCALE: 2:1 | WEIGHT: | SHEET 1 OF 1

SOLIDWORKS Educational Product. For Instructional Use Only.

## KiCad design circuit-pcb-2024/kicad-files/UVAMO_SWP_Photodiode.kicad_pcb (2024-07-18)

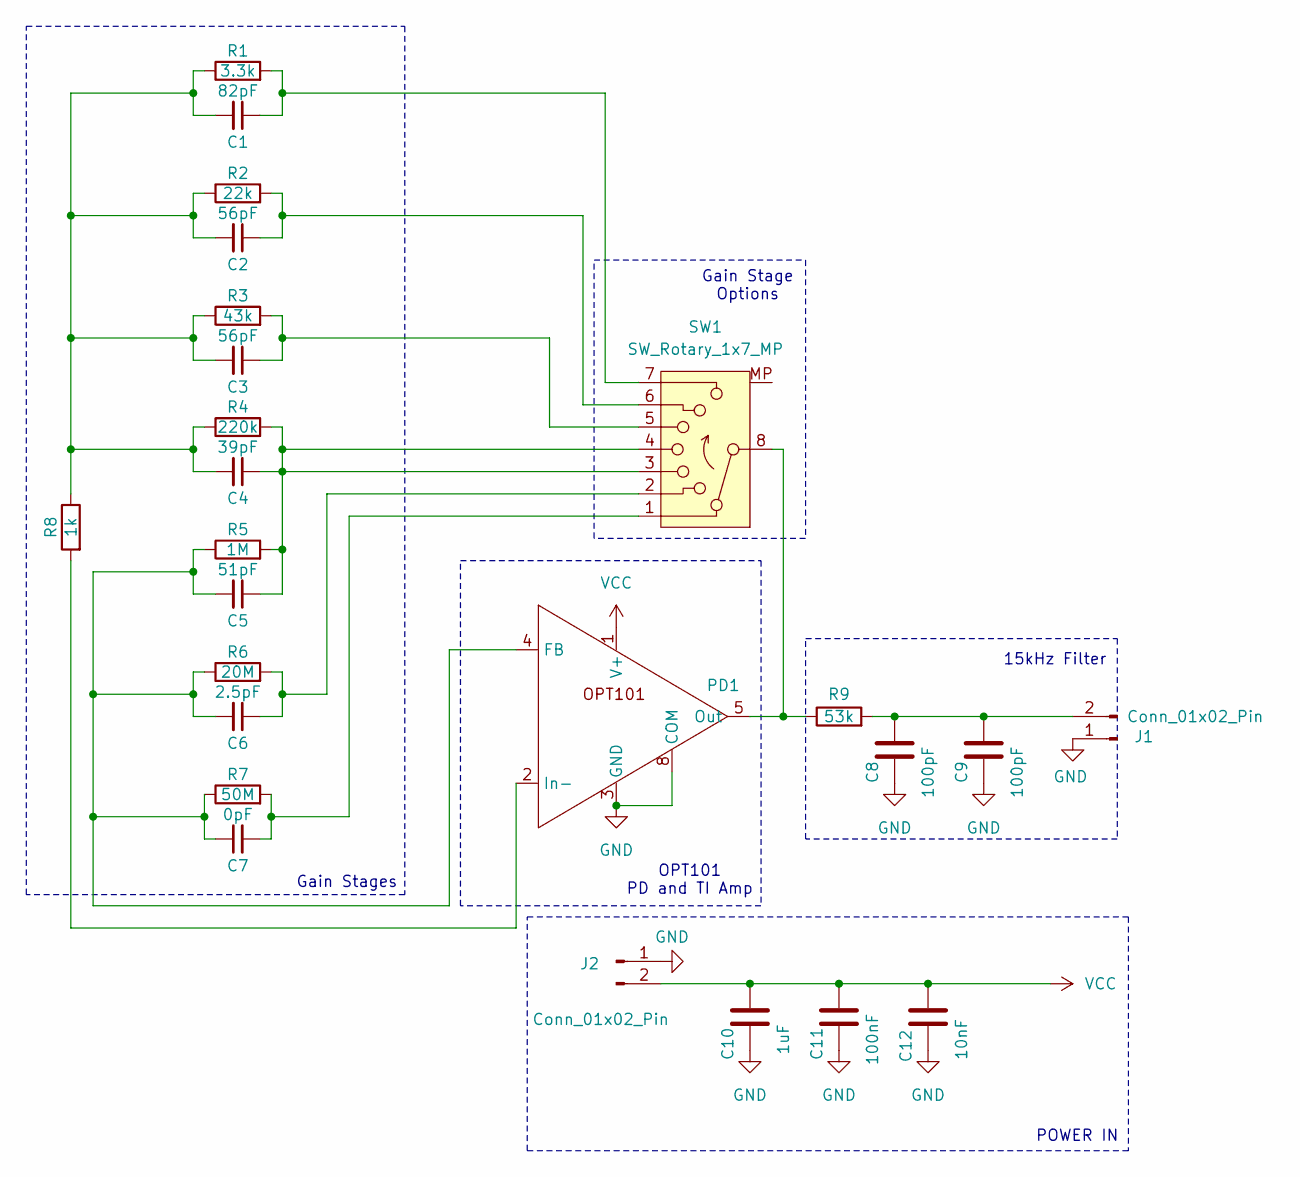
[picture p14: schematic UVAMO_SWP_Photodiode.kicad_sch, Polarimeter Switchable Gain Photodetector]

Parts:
C1: 82pF; C_0603_1608Metric_Pad1.08x0.95mm_HandSolder; DigiKey Part Number 478-KGM15ACG1H820JTCT-ND
C2, C3: 56pF; C_0603_1608Metric_Pad1.08x0.95mm_HandSolder; DigiKey Part Number 478-KGM15ACG1H560JTCT-ND
C4: 39pF; C_0603_1608Metric_Pad1.08x0.95mm_HandSolder; DigiKey Part Number 478-KGM15ACG1H390JTCT-ND
C5: 51pF; C_0603_1608Metric_Pad1.08x0.95mm_HandSolder; DigiKey Part Number 478-10326-1-ND
C6: 2.5pF; C_0603_1608Metric_Pad1.08x0.95mm_HandSolder; DigiKey Part Number 13-CC0603BRNPO9BN2R5CT-ND
C7: 0pF; C_0603_1608Metric_Pad1.08x0.95mm_HandSolder
C8, C9: 100pF; C_0603_1608Metric_Pad1.08x0.95mm_HandSolder; DigiKey Part Number 311-1069-1-ND
C10: 1uF; C_2225_5664Metric_Pad1.80x6.60mm_HandSolder; DigiKey Part Number 445-2304-1-ND
C11: 100nF; C_0805_2012Metric_Pad1.18x1.45mm_HandSolder; DigiKey Part Number 311-1140-1-ND
C12: 10nF; C_0603_1608Metric_Pad1.08x0.95mm_HandSolder; DigiKey Part Number 490-4781-1-ND
J1, J2: Conn_01x02_Pin; Molex_KK-254_AE-6410-02A_1x02_P2.54mm_Vertical; DigiKey Part Number 900-0022232021-ND
PD1: DIP-8_W7.62mm_LongPads; DigiKey Part Number 296-23090-5-ND
R1: 3.3k; R_0603_1608Metric_Pad0.98x0.95mm_HandSolder; DigiKey Part Number 311-3.30KHRCT-ND
R2: 22k; R_0603_1608Metric_Pad0.98x0.95mm_HandSolder; DigiKey Part Number 311-22KGRCT-ND
R3: 43k; R_0603_1608Metric_Pad0.98x0.95mm_HandSolder; DigiKey Part Number 311-43.0KHRCT-ND
R4: 220k; R_0603_1608Metric_Pad0.98x0.95mm_HandSolder; DigiKey Part Number 311-220KGRCT-ND
R5: 1M; R_0603_1608Metric_Pad0.98x0.95mm_HandSolder; DigiKey Part Number 311-1.00MHRCT-ND
R6: 20M; R_0603_1608Metric_Pad0.98x0.95mm_HandSolder; DigiKey Part Number 13-RC0603JR-0720MLCT-ND
R7: 50M; R_0603_1608Metric_Pad0.98x0.95mm_HandSolder; DigiKey Part Number 541-47MAHCT-ND
R8: 1k; R_0603_1608Metric_Pad0.98x0.95mm_HandSolder; DigiKey Part Number 311-1.00KHRCT-ND
R9: 53k; R_0603_1608Metric_Pad0.98x0.95mm_HandSolder; DigiKey Part Number 311-53.6KHRCT-ND
SW1: SW_Rotary_1x7_MP; RM107-RotarySwitch; DigiKey Part Number CKN10705-ND

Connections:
GND: C8.2, C9.2, C10.2, C11.2, C12.2, J1.1, J2.1, PD1.3 (GND), PD1.8 (COM)
unnamed: C1.1, R1.2, SW1.7
unnamed: C1.2, C2.2, C3.2, C4.2, R1.1, R2.1, R3.1, R4.1, R8.1
unnamed: C2.1, R2.2, SW1.6
unnamed: C3.1, R3.2, SW1.5
unnamed: C4.1, C5.1, R4.2, R5.2, SW1.3, SW1.4
unnamed: C6.1, R6.2, SW1.2
unnamed: C7.2, R7.2, SW1.1
unnamed: C8.1, C9.1, J1.2, R9.2
unnamed: C5.2, C6.2, C7.1, PD1.4 (FB), R5.1, R6.1, R7.1
unnamed: PD1.2 (In-), R8.2
unnamed: PD1.5 (Out), R9.1, SW1.8
VCC: C10.1, C11.1, C12.1, J2.2, PD1.1 (V+)

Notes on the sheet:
Gain Stages
OPT101 PD and TI Amp
Gain Stage Options
POWER IN
15kHz Filter

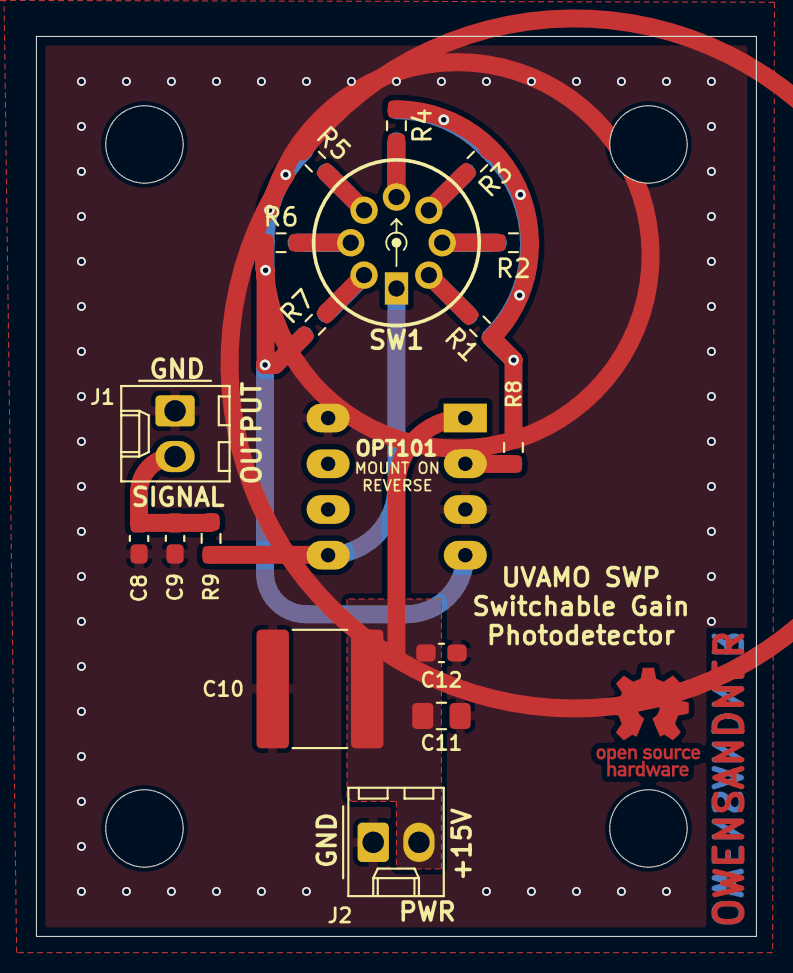
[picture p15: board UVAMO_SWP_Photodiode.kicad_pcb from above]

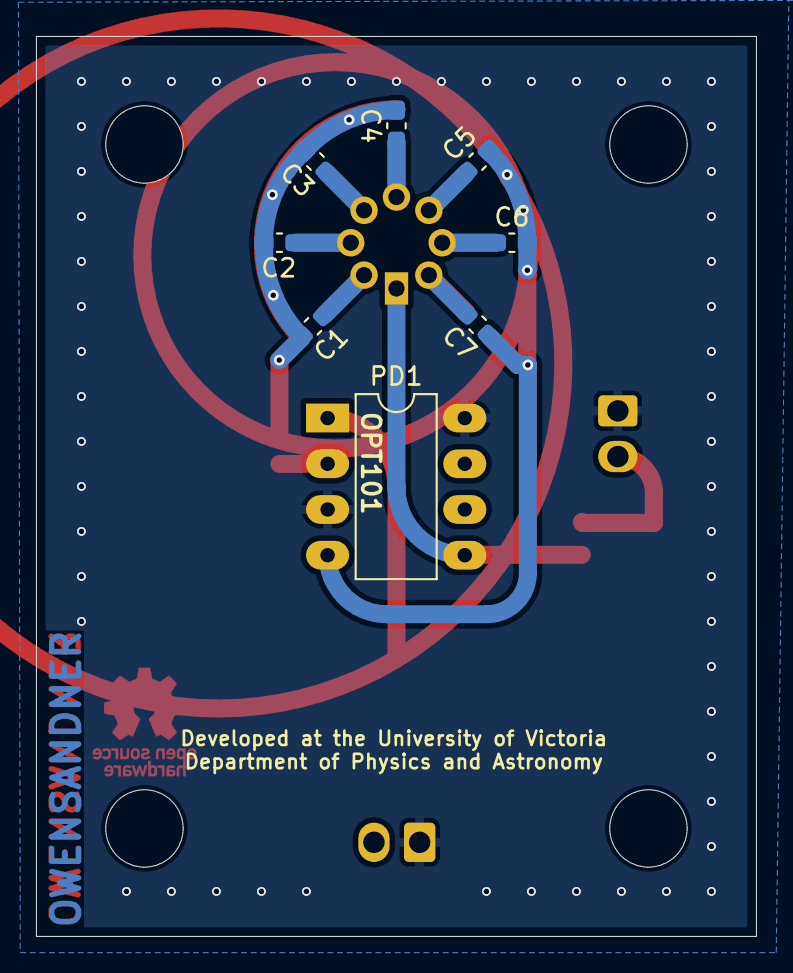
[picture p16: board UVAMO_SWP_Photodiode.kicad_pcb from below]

Board: 2 copper layers, 40.0 x 50.0 mm, 29 parts (8 on the bottom side), 13 nets.

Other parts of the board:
H1, H2, H3, H4: MountingHole; MountingHole_4.3mm_M4

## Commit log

2023-03-30 Created directory for pcb circuit and added kicad files.
    [polarimeter.kicad_pcb, polarimeter.kicad_sch]
2023-07-18 Cleaning raspberry pi for ease of use. All future pushes should be conducted from personal computers--the raspeberry pi will only be updated with frequent pulls.
2024-07-15 removed old pcb, exraneous files
    [polarimeter.kicad_pcb, polarimeter.kicad_sch]
2024-07-15 Create new PCB directory as well as README.md
    Wrote up a short README, will add PCB files and a guide for the PCB
2024-07-15 Added KiCad files
    [UVAMO_SWP_Photodiode.kicad_pcb, UVAMO_SWP_Photodiode.kicad_sch]
2024-07-15 Added order files
    [SWPBOM.csv]
2024-07-18 Updated PCB Files
    Found issue in old PCB. Updated all related files
    [SWPBOM.csv, UVAMO_SWP_Photodiode.kicad_pcb, UVAMO_SWP_Photodiode.kicad_sch]
2024-07-18 Updated comments in calibrate_trigger_delay.py
    Added missing comments, adjusted one variable name to be identifiable.
2024-07-19 Delete circuit-pcb-2024/SWPPhotodiodeGuide.pdf
    Uploading new guide for updated circuit
2024-07-19 Added Calibrate Background
2024-07-19 Update with main
    [SWPBOM.csv, UVAMO_SWP_Photodiode.kicad_pcb, UVAMO_SWP_Photodiode.kicad_sch]
2024-07-19 Added Filtering
2024-07-22 Added Motor Jitter Estimation
2024-07-23 Updated Filters
2024-07-24 Added some CAD files, added data logging functionality, and created test script for brewster experiment
    [Polarimeter_DiodeHolder_Base.STEP, Polarimeter_DiodeHolder_Top.STEP, Test_Data.csv]
2024-07-29 Organization and last touches on existing code
    [Polarimeter_DiodeHolder_Base.STEP, Polarimeter_DiodeHolder_Top.STEP, Test_Data.csv, Test_Data2.csv]
2024-07-30 Initial Commit. Basic framework. Not functional.
